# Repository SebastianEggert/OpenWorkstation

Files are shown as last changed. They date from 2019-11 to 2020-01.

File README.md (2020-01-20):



# OpenWorkstation
 An open source and modular workstation concept for life science automation.

 * [Overview](#overview)
 * [OpenWorkstation API](#api)
 * [Development Status](#development_status)
 * [Getting Started](#getting_started)
 * [Contributing](#contributing)

## Overview

We present a general Open Source Hardware concept to develop scientific equipment. The general setup can be customized to fit diverse experimental requirements by adding different numbers and kinds of hardware modules to execute the desired functionality. Within these modules, each hardware module as well as the configuration of the hardware modules can be specifically customized according to the experimental requirements. This ‘drag and drop’ approach enables a high degree of versatility, since the components as well as their configuration can be customized to fit the given requirements.

Specifically, the OpenWorkstation concept provides the following features:

 * Simple and fast development of customized hardware modules
 * Modularity to combine different open source projects
 * Available API to operate modules
 * Hardware and software files are freely accessible

 <p align="center">
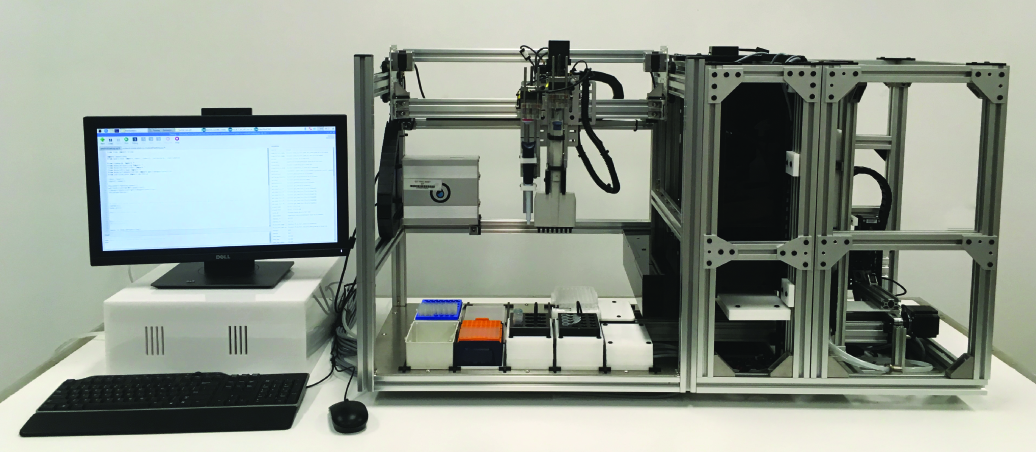
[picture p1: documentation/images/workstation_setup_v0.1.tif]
 </p>

## OpenWorkstation API

Building upon the [Opentrons API](https://github.com/Opentrons/opentrons), the OpenWorkstation API is a simple Python framework designed to allow the operation of hardware modules.

If you are familiar with python and comfortable running ``pip``, you can install OpenWorkstation API by running:

```
pip install openworkstation
```

## Development status

The OpenWorkstation project is an open source project. The concept was developed in the labs of the [ARC Industrial Transformation Training Centre in Additive Biomanufacturing](http://additivebiomanufacturing.org) to simplify the design and development of automated solutions. The OpenWorkstation project remains under active development and new software as well as hardware features continue to be integrated.

Please do no hesitate to [get in touch](mailto:s.eggert@qut.edu.au) to provide feedback and discuss potential applications.

## Getting started

The documentation is divided into the following sections:

 * [Concept](documentation/concept.md) for general information
 * [Pre-requisites and installation](documentation/installation.md) describes what you will need to install the OpenWorkstation API
 * [Programming](documentation/programming.md) provides detailed instructions on writing scripts to operate the modules
 * [Developed module files](hardware/README.md) are available for the present workstation
 * [CAD part library](hardware/README.md) is provided to accelerate the development process for new module
 * [Development plan](documentation/dev_plan.md) outlines future work packages

## Contributing

We are looking for contributors!

[Get in touch](mailto:s.eggert@qut.edu.au)

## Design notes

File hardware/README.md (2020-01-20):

## Hardware

The hardware section is divided into CAD files (SolidWorks) used to build the presented workstation (incl modules) and a parts library to accelerate the development process for new modules in the future.

All hardware files are available for the presented workstation:

 * [Assembled workstation](workstation)
 * [Pipetting module](modulePipetting)  
 * [Crosslinker module](moduleCrosslinker)
 * [Storage module](moduleStorage)
 * [Transport module](moduleTransport)
 * [Base frame](base-frame)

The following libraries are available to support users during the development of new module:

 * [Aluminium profiles](aluminium-profiles)
 * [Module frames](moduleFrame)
 * [OpenBuilds parts](OpenBuilds)

OpenBuilds provides additional support via their [SolidWorks part library](https://openbuilds.com/projectresources/solidworks-2014-parts-library.160/) and the uploaded models on [GrabCAD](https://grabcad.com/openbuilds-1/models).

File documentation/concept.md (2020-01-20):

## Concept

Inspired by industrial assembly lines, we aimed for an approach to engineer a workstation where samples are being transported through customizable and reconfigurable modules. To do so, we developed (i) a modular concept, (ii) customizable hardware modules, and (iii) fully accessible application programming interface (API).

We describe a setup with a modular architecture, wherein we use one module respectively to implement a set of diverse functional elements. The base setup of the assembly line-inspired concept accommodates a pipetting and a transport module as essential elements. A transport module is required to move samples through the modules and, thereby, connects the implemented hardware modules with each other. A pipetting module is installed for essential pipetting operations which are required for almost every in vitro study. This general set up can then be customized to suit diverse experimental requirements by adding different numbers and kinds of hardware modules executing the desired functionality. Within these modules, each hardware module as well as the configuration of the hardware modules can be individually customized according to the experimental requirements. This ‘drag and drop’ approach enables a high degree of versatility, since the components as well as their configuration can be customized to fit the given requirements, including the option to remove components from the platform non-destructively without interfering with the functional operation of the other modules.

<p align="center">
</p>

## General module description

#### Computational module
A computer is utilized to operate the workstation by providing an interface and sending the experimental protocol to the implemented control boards which forward commands to the functional parts of the hardware modules. A Python API has been developed to write protocol scripts to operate the entire workstation, and, thereby, all hardware modules in a synchronized mode. Python has been selected as the main programming language, since it is open source and a high-level and general-purpose dynamic language that focuses on code readability. Some of Python’s main advantages are (i) the extensive support libraries; (ii) the numerous third-party modules via the Python Package Index (PyPI) to enable interactions with other languages and platforms; (iii) the open source character and the community-driven development to facilitate collaborations and ease of use; and (iv) the increased productivity to build scalable multi-protocol network applications.

#### Control board module
A control board translates the received protocol script into a language to operate the functional components of the hardware modules. We selected the smoothieboard (The Smoothie Project, http://smoothieware.org) as the control board module due to the range of available sizes (e.g. from 3x to 5x axis control), the numerous capabilities (e.g. up to 5x axis control with 1/32 microstepping, 6x end stops, up to 3x MOSFETs with 12.5A max, and 3x MOSFETs with 3A max, ethernet and USB connections), the 32-bit microcontroller, the available documentation, and the overall quality to price ratio. The Smoothie Project is an open source project supported by the community to design open source hardware controllers with open source firmware (https://github.com/Smoothieware). The following motion control boards can be recommended as alternatives, but have not been tested and might require additional software engineering for successful implementation: Duet3D , Panucatt Azteeg X5 GT , TinyG CNC Controller Board .

#### Hardware modules
The customized hardware modules operate a set of specific functions required to execute the experiment. The combination of functional components into one hardware module introduces an efficient and agile approach, since a single module can be easily modified without interfering with other modules. To do so, functional components are integrated into an aluminium frame to enable easy module handling and provide a robust solution for moving parts. Moreover, the various connection modes of the aluminium profiles (e.g. t-slots, nuts, threated holes, corner brackets, etc.) enable fast and inexpensive design iterations. Pre-configured aluminium frames as well as assembled mechanical parts (e.g. linear stages) are available for developers as ready-to-use assemblies to support and accelerate the design and development process. Under section 2.4, we demonstrate the feasibility for customized hardware module development and, subsequently, successful adoption of this concept for laboratory automation in the context of a case study.

#### Monitoring modules
As monitoring capability, we understand the measurement of process variables either continuously and/or repeatedly during the course of the experiment. In general, monitoring modules may include camera-based systems or various sensor types (e.g. temperature, pH, oxygen, lactate, etc.) to record the variables and document the changes over time. Implemented functions can also be used in the sense of an in-process control unit to automatically adjust operational variables via advanced process algorithms. Such in-process control units ensure consistent product quality or reach defined product output specifications.

<p align="center">
</p>

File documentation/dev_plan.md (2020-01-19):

## Development Plan

The development plan will provide an overview of current work and future projects.

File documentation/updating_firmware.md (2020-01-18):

# Updating Firmware of Motorcontroller

The project is using smoothieboards to execute implemented functions. The configuration of the connected peripherals (e.g. stepper motor) is stored on the smoothieboard's SD card and has to be updated initially. When parts with a different specification (e.g. step size of a stepper motor) are used, the configuration files have to be modified to accommodate the physical changes. A list of most configuration options is provided by the Smoothie Project (http://smoothieware.org/configuration-options).

The configuration for the developed modules with the implemented parts can be found in the design files section.

Building upon the Opentrons open source products (https://opentrons.com), this project is using Opentrons' firmware for the smoothieboard.

### Download Files

[Download the zipped files from here](https://github.com/opentrons/smoothie-config/archive/1.2.0.zip) and unpack them.

### Update config file
Open `config` file, update specifications for your developed module, such as step size for stepper motor), and save file.

### Update files on the smoothieboard's SD card

Open the SD card of your smoothieboard and copy the `FIRMWARE.CUR` (downloaded from Github) and `config` (updated in the previous step) files onto the SD card.

### Restart

Insert the SD card into the smoothieboard and restart the smoothieboard by connecting the USB or power supply. The board will read the `firmware.bin` file, then save it as `FIRMWARE.CUR`. Functionalities are executed based on the updated `config` file.

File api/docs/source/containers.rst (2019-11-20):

.. _containers:

######################
Containers
######################

We spend a fair amount of time organizing and counting wells when writing Python protocols. This section describes the different ways we can access wells and groups of wells.

************************************

******************
Labware Library
******************

The opentrons API comes with many common labware containers built in. These containers can be loaded into you Python protocol using the ``containers.load()`` method, and the specific name of the labware you need.

`Check out this webpage`__ to see a visualization of all the API's current built-in containers.

__ https://andysigler.github.io/ot-api-containerviz/

Below are a list of some of the most commonly used containers in the API, as well as images for how they look.

If you are interested in using your own container that is not included in the API, please take a look at how to create custom containers using ``containers.create()``, or contact opentrons Support.

.. note::

    All names are case-sensitive, copying and pasting from this list into the protocol editor will ensure no errors are made.

**********************

Point
=====

Use ``point`` when there is only one position per container, such as the trash or a scale. 

.. code-block:: python

    container.load('point', slot)

You can access the point position as ``container.wells('A1')`` or ``container.wells(0)``.

**********************

Tipracks
==========

tiprack-10ul
-------------

Tip rack for a 10 uL pipette (single or 8-channel)

.. code-block:: python

    container.load('tiprack-10ul', slot)

**Accessing Tips:** *single channel* ``['A1']-['H12']``, *8-channel* ``['A1']-['A12']``

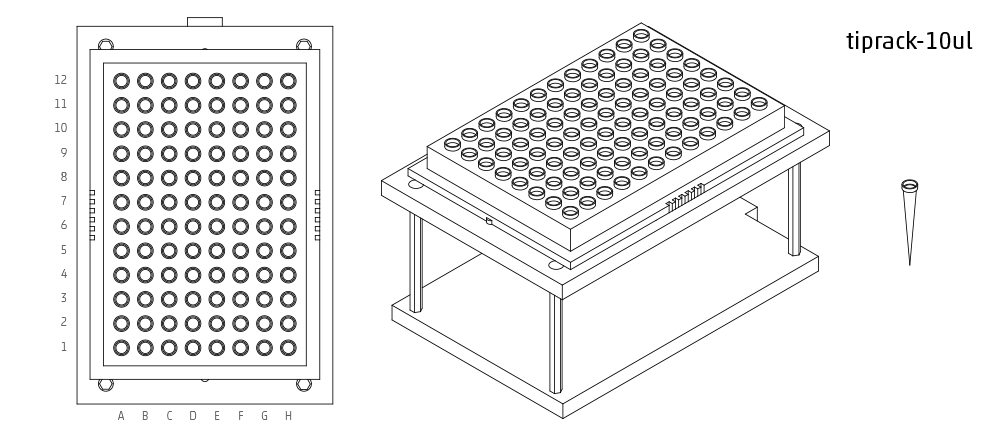
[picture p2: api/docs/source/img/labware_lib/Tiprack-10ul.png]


tiprack-10ul-H
--------------

Tip rack for a single channel 10 uL pipette when the pipette is in the center position.  Set initial position to H1, and the pipette will use all the tips on the right hand side (E-H, 1-12)

.. code-block:: python

    container.load('tiprack-10ul-H', slot)

**Accessing Tips:** *single channel* ``['E-H, 1-12']``

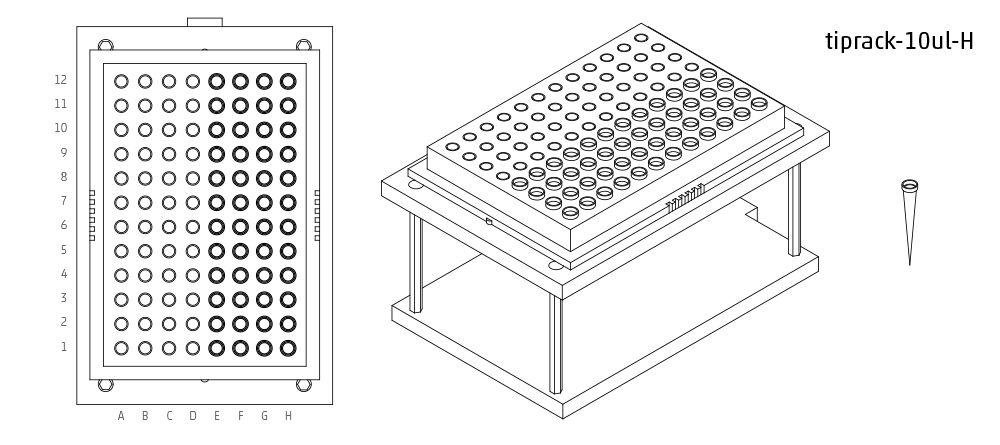
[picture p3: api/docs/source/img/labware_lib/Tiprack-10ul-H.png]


tiprack-200ul
-------------

Tip rack for a 200 or 300 uL pipette (single or 8-channel)

.. code-block:: python

    container.load('tiprack-200ul', slot)

**Accessing Tips:** *single channel* ``['A1']-['H12']``, *8-channel* ``['A1']-['A12']``

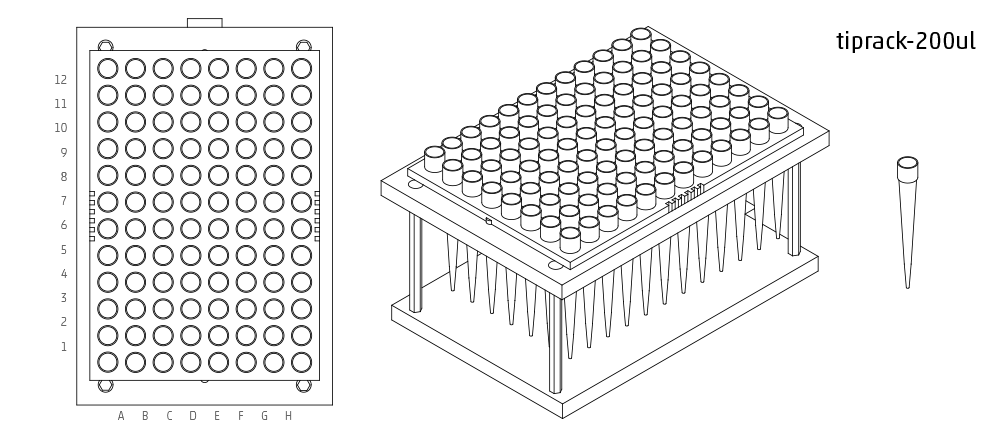
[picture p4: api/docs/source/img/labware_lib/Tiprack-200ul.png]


tiprack-1000ul
--------------

Tip rack for a 1000 uL pipette (single or 8-channel)

.. code-block:: python

    container.load('tiprack-1000ul', slot)

**Accessing Tips:** *single channel* ``['A1']-['H12']``, *8-channel* ``['A1']-['A12']``

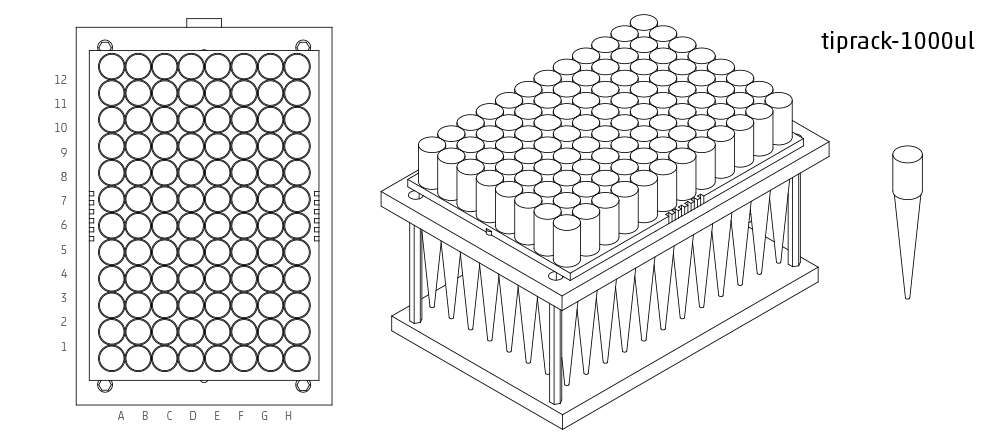
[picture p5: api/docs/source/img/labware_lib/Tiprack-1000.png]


tiprack-1000ul-chem
-------------------

Tip rack for 1000ul chem (10x10)

.. code-block:: python

    container.load('tiprack-1000ul-chem', slot)

**Accessing Tips:** *single channel* ``[0]-[99]``

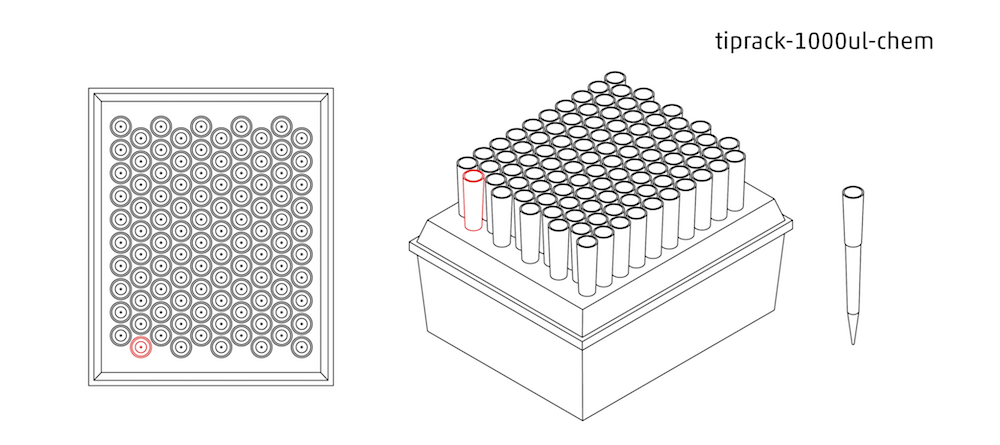
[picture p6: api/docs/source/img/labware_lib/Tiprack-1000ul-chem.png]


**********************

Troughs
========

trough-12row
-------------

12 row reservoir

.. code-block:: python

    container.load('trough-12row', slot)

**Accessing Rows:** *single channel* ``['A1']-['A12']``, *8-channel* ``['A1']-['A12']``

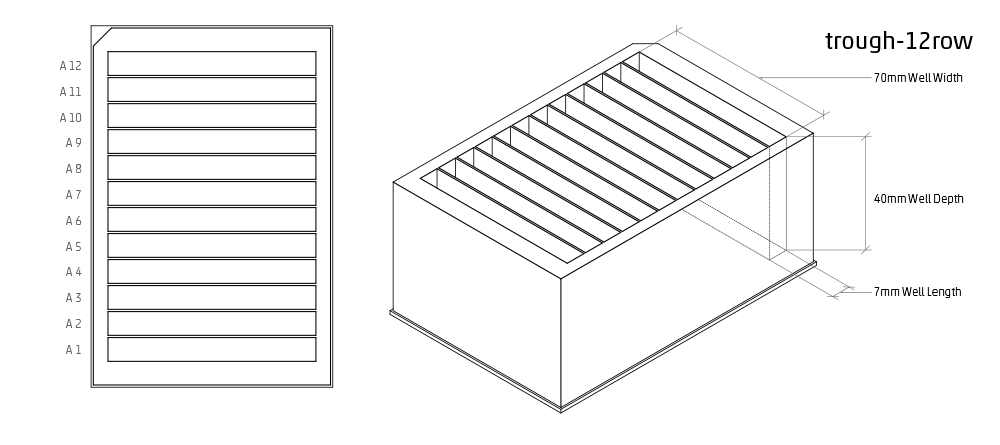
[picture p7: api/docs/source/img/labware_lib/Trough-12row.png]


**********************

Tube Racks
==========

tube-rack-.75ml
-------------

4x6 rack that holds .75 mL microcentrifuge tubes
(A1, A1-D6)

.. code-block:: python

    container.load('tube-rack-.75ml', slot)

**Accessing Tubes:** *single channel* ``['A1']-['D6']``

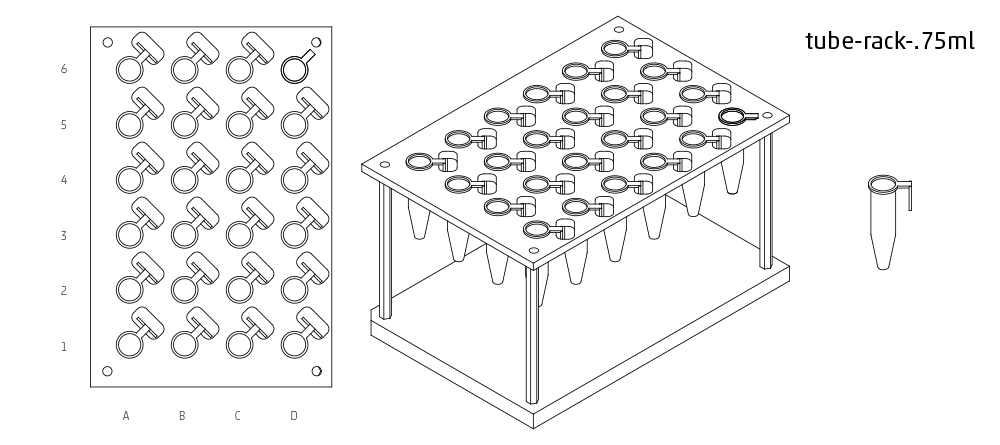
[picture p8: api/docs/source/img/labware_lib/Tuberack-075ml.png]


tube-rack-2ml
-------------

4x6 rack that holds 1.5 mL microcentrifuge tubes and 2 mL microcentrifuge tubes

.. code-block:: python

    container.load('tube-rack-2ml', slot)

**Accessing Tubes:** *single channel* ``['A1']-['D6']``

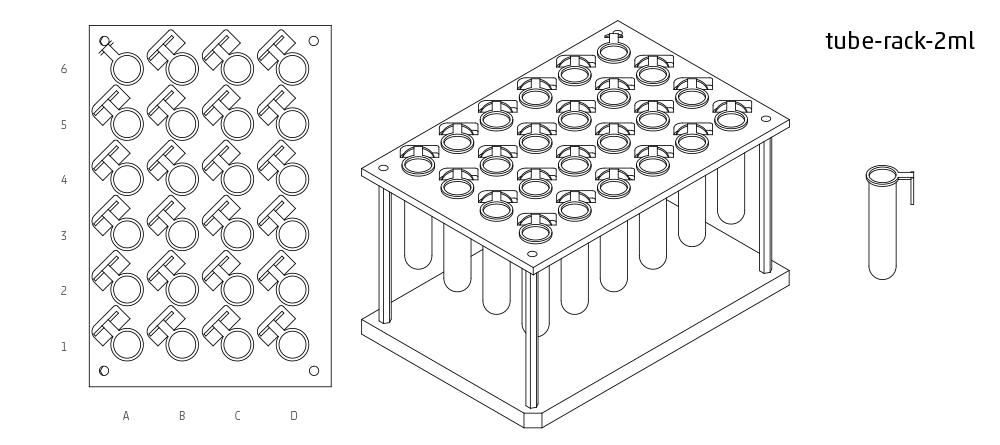
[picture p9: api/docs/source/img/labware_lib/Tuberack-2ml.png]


tube-rack-15_50ml
------------------

rack that holds 6 15 mL tubes and 4 50 mL tubes

.. code-block:: python

    container.load('tube-rack-15_50ml', slot)

**Accessing Tubes:** *single channel* ``['A1']-['A3'], ['B1']-['B3'], ['C1']-['C2'], ['D1']-['D2']``

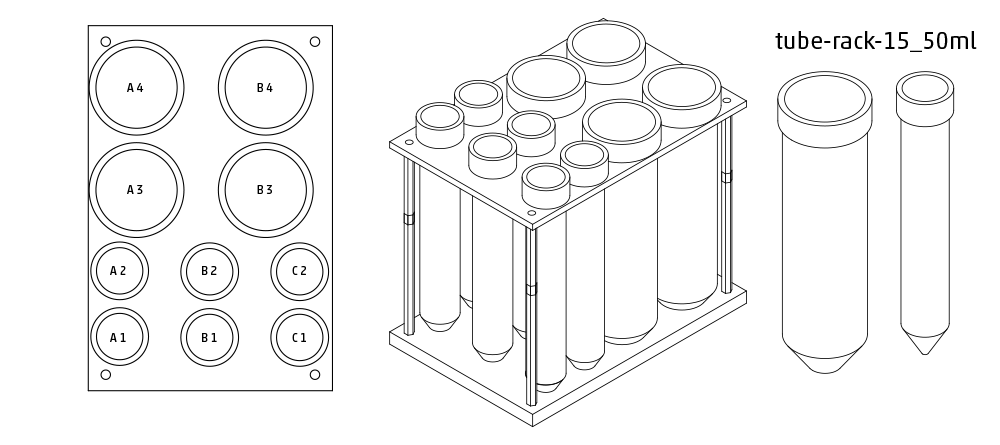
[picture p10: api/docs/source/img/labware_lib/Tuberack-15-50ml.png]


Plates
=======

96-deep-well
-------------

See dimensions in diagram below.

.. code-block:: python

    container.load('96-deep-well', slot)

**Accessing Wells:** *single channel* ``['A1']-['H12']``, *8-channel* ``['A1']-['A12']``

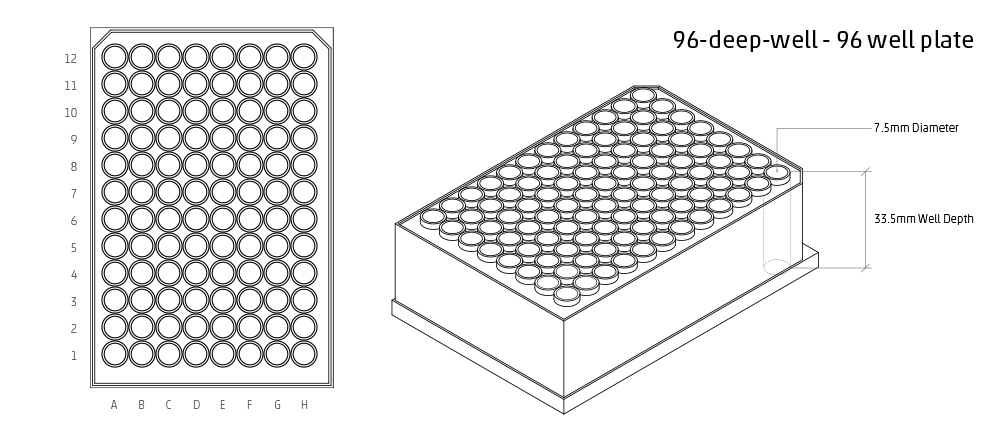
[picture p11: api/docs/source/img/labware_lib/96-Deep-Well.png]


96-PCR-tall
-------------

See dimensions in diagram below.

.. code-block:: python

    container.load('96-PCR-tall', slot)

**Accessing Wells:** *single channel* ``['A1']-['H12']``, *8-channel* ``['A1']-['A12']``

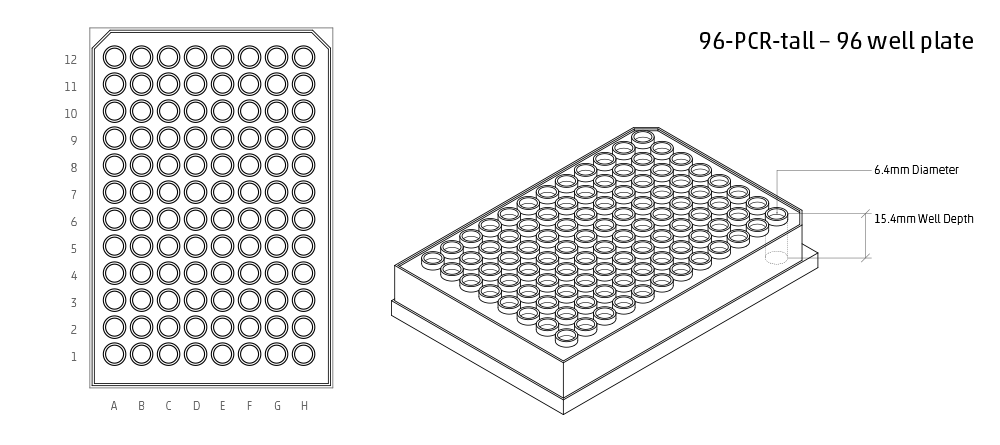
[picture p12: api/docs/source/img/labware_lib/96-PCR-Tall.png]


96-PCR-flat
-------------

See dimensions in diagram below.

.. code-block:: python

    container.load('96-PCR-flat', slot)

**Accessing Wells:** *single channel* ``['A1']-['H12']``, *8-channel* ``['A1']-['A12']``

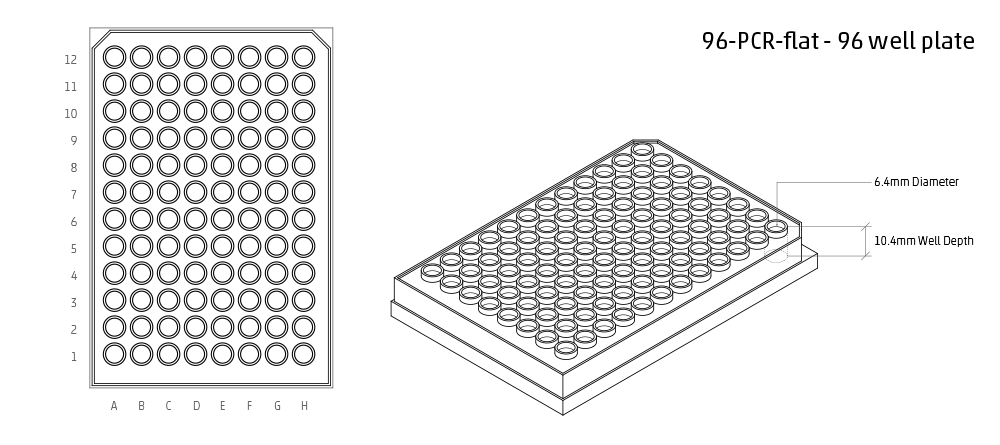
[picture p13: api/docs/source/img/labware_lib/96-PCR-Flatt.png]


PCR-strip-tall
----------------

See dimensions in diagram below.

.. code-block:: python

    container.load('PCR-strip-tall', slot)

**Accessing Wells:** *single channel* ``['A1']-['A8']``, *8-channel* ``['A1']``

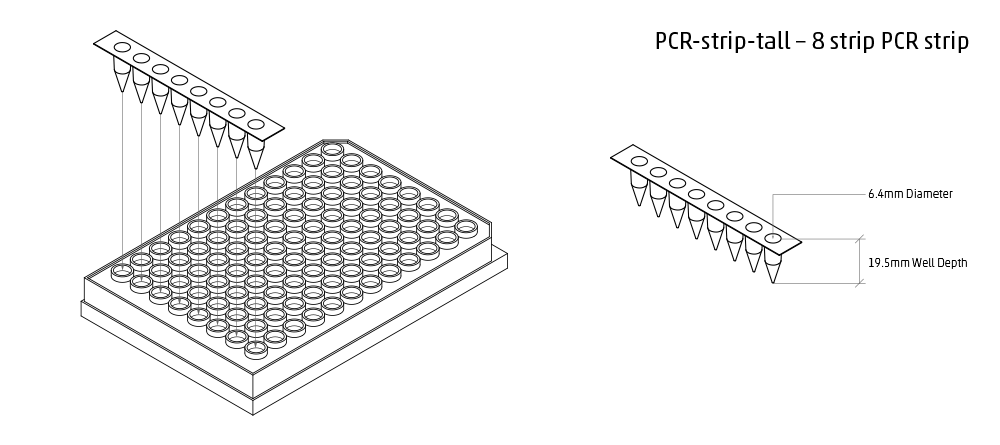
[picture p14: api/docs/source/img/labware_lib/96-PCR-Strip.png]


384-plate
----------

See dimensions in diagram below.

.. code-block:: python

    container.load('384-plate', slot)

**Accessing Wells:** *single channel* ``['A1']-['P24']``, *multi-channel* ``['A1']-['A24]``

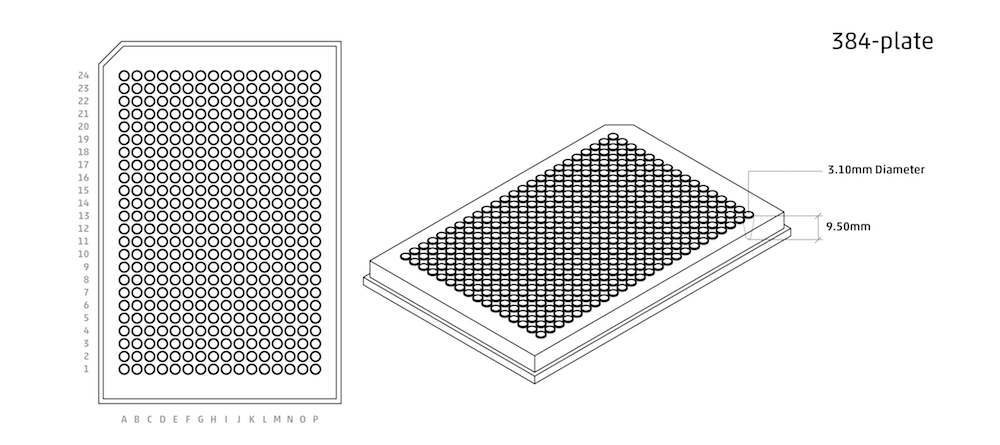
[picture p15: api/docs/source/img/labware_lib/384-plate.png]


**********************

.. testsetup:: containers

    from opentrons import containers, robot
    robot.reset()

**************
Containers
**************

The containers module allows you to load common labware into your protocol. `Go here`__ to see a visualization of all built-in containers.

__ https://andysigler.github.io/ot-api-containerviz/

.. testcode:: containers

    '''
    Examples in this section require the following
    '''
    from opentrons import containers

List
====

Once the container module is loaded, you can see a list of all containers currently inside the API by calling ``containers.list()``

.. testcode:: containers

    containers.list()

Load
====

Labware is loaded with two arguments: 1) the container type, and 2) the deck slot it will be placed in on the robot.

.. testcode:: containers

    p = containers.load('96-flat', 'B1')

A third optional argument can be used to give a container a unique name.

.. testcode:: containers

    p = containers.load('96-flat', 'B1', 'any-name-you-want')

Unique names are useful in a few scenarios. First, they allow the container to have independant calibration data from other containers in the same slot. In the example above, the container named 'any-name-you-want' will assume different calibration data from the unnamed plate, even though they are the same type and in the same slot.

.. note::

    Calibration data refers to the saved positions for each container on deck, and is a part of the `opentrons App calibration procedure`__.

__ https://opentrons.com/getting-started/calibrate-deck

Names can also be used to place multiple containers in the same slot all at once. For example, the flasks below are all placed in slot D1. So in order for the opentrons API to tell them apart, we have given them each a unique name.

.. testcode:: containers

    fa = containers.load('T25-flask', 'D1', 'flask_a')
    fb = containers.load('T25-flask', 'D1', 'flask_b')
    fc = containers.load('T25-flask', 'D1', 'flask_c')

Create
======

In addition to the default containers that come with the opentrons API, you can create your own custom containers.

Through the API's call containers.create(), you can create simple grid containers, which consist of circular wells arranged in columns and rows.

.. testcode:: containers

    containers.create(
        '3x6_plate',                    # name of you container
        grid=(3, 6),                    # specify amount of (columns, rows)
        spacing=(12, 12),               # distances (mm) between each (column, row)
        diameter=5,                     # diameter (mm) of each well on the plate
        depth=10)                       # depth (mm) of each well on the plate

When you create your custom container, then it will be saved for later use under the name you've given it. This means you can use containers.load() to use the custom container you've created in this and any future protocol.

.. testcode:: containers

    custom_plate = containers.load('3x6_plate', 'D1')

    for well in custom_plate.wells():
        print(well)

will print out...

.. testoutput:: containers
    :options: -ELLIPSIS, +NORMALIZE_WHITESPACE

    <Well A1>
    <Well B1>
    <Well C1>
    <Well A2>
    <Well B2>
    <Well C2>
    <Well A3>
    <Well B3>
    <Well C3>
    <Well A4>
    <Well B4>
    <Well C4>
    <Well A5>
    <Well B5>
    <Well C5>
    <Well A6>
    <Well B6>
    <Well C6>

.. testsetup:: pipettes

    from opentrons import instruments, robot
    robot.reset()

**********************

.. testsetup:: individualwells

    from opentrons import containers, robot

    robot.reset()
    plate = containers.load('96-flat', 'A1')

******************
Accessing Wells
******************

**********************

Individual Wells
================

When writing a protocol using the API, you will be spending most of your time selecting which wells to transfer liquids to and from.

The OT-One deck and containers are all set up with the same coordinate system - numbered rows and lettered columns.

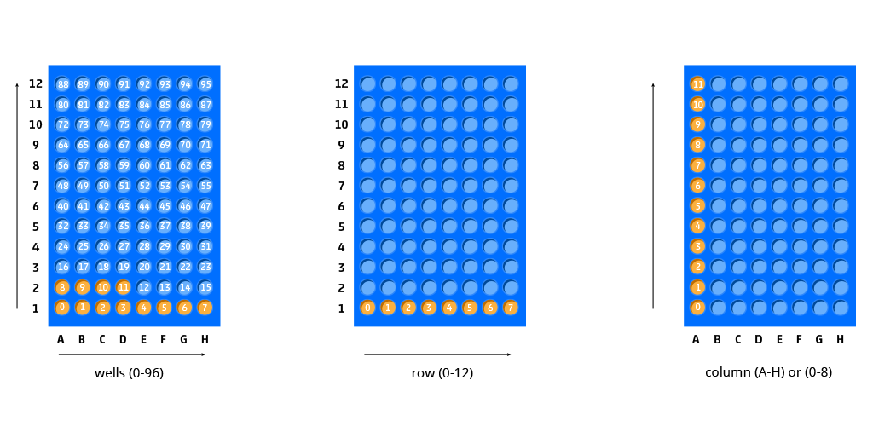
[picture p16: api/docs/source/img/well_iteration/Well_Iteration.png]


.. testcode:: individualwells
    
    '''
    Examples in this section expect the following
    '''
    from opentrons import containers

    plate = containers.load('96-flat', 'A1')

Wells by Name
-------------

Once a container is loaded into your protocol, you can easily access the many wells within it using ``wells()`` method. ``wells()`` takes the name of the well as an argument, and will return the well at that location.

.. testcode:: individualwells

    plate.wells('A1')
    plate.wells('H12')

Wells by Index
--------------

Wells can be referenced by their "string" name, as demonstrated above. However, they can also be referenced with zero-indexing, with the first well in a container being at position 0.

.. testcode:: individualwells

    plate.wells(0)   # well A1
    plate.wells(95)  # well H12
    plate.wells(-1)  # well H12 (Python let's you do this)

Columns and Rows
----------------

A container's wells are organized within a series of columns and rows, which are also labelled on standard labware. In the API, columns are given letter names (``'A'`` through ``'H'`` for example) and go left to right, while rows are given numbered names (``'1'`` through ``'8'`` for example) and go from front to back.
You can access a specific row or column by using the ``rows()`` and ``cols()`` methods on a container. These will return all wells within that row or column.

.. testcode:: individualwells

    column = plate.cols('A')
    row = plate.rows('1')

    print('Column "A" has', len(column), 'wells')
    print('Row "1" has', len(row), 'wells')

will print out...

.. testoutput:: individualwells
    :options: -ELLIPSIS, +NORMALIZE_WHITESPACE

    Column "A" has 12 wells
    Row "1" has 8 wells

The ``rows()`` or ``cols()`` methods can be used in combination with the ``wells()`` method to access wells within that row or column. In the example below, both lines refer to well ``'A1'``.

.. testcode:: individualwells

    plate.cols('A').wells('1')
    plate.rows('1').wells('A')

**********************

.. testsetup:: multiwells

    from opentrons import containers, robot

    robot.reset()
    plate = containers.load('96-flat', 'A1')

Multiple Wells
==============

If we had to reference each well one at a time, our protocols could get very very long.

When describing a liquid transfer, we can point to groups of wells for the liquid's source and/or destination. Or, we can get a group of wells that we want to loop through.

.. testcode:: multiwells
    
    '''
    Examples in this section expect the following
    '''
    from opentrons import containers

    plate = containers.load('96-flat', 'B1')

Wells
-----

The ``wells()`` method can return a single well, or it can return a list of wells when multiple arguments are passed.

Here is an example or accessing a list of wells, each specified by name:

.. testcode:: multiwells

    w = plate.wells('A1', 'B2', 'C3', 'H12')

    print(w)

will print out...

.. testoutput:: multiwells
    :options: -ELLIPSIS, +NORMALIZE_WHITESPACE

    <WellSeries: <Well A1><Well B2><Well C3><Well H12>>

Multiple wells can be treated just like a normal Python list, and can be iterated through:

.. testcode:: multiwells

    for w in plate.wells('A1', 'B2', 'C3', 'H12'):
        print(w)

will print out...

.. testoutput:: multiwells
    :options: -ELLIPSIS, +NORMALIZE_WHITESPACE

    <Well A1>
    <Well B2>
    <Well C3>
    <Well H12>

Wells To
--------

Instead of having to list the name of every well, we can also create a range of wells with a start and end point. The first argument is the starting well, and the ``to=`` argument is the last well.

.. testcode:: multiwells
    
    for w in plate.wells('A1', to='H1'):
        print(w)

will print out...

.. testoutput:: multiwells
    :options: -ELLIPSIS, +NORMALIZE_WHITESPACE

    <Well A1>
    <Well B1>
    <Well C1>
    <Well D1>
    <Well E1>
    <Well F1>
    <Well G1>
    <Well H1>

Not only can we get every well between the start and end positions, but we can also set the ``step=`` size. The example below will access every 2nd well between ``'A1'`` and ``'H'``:

.. testcode:: multiwells
    
    for w in plate.wells('A1', to='H1', step=2):
        print(w)

will print out...

.. testoutput:: multiwells
    :options: -ELLIPSIS, +NORMALIZE_WHITESPACE

    <Well A1>
    <Well C1>
    <Well E1>
    <Well G1>

These lists of wells can also move in the reverse direction along your container. For example, setting the ``to=`` argument to a well that comes before the starting position is allowed:

.. testcode:: multiwells
    
    for w in plate.wells('H1', to='A1', step=2):
        print(w)

will print out...

.. testoutput:: multiwells
    :options: -ELLIPSIS, +NORMALIZE_WHITESPACE

    <Well H1>
    <Well F1>
    <Well D1>
    <Well B1>

Wells Length
------------

Another way you can create a list of wells is by specifying the length= of the well list you need, in addition to the starting point. The example below will return eight wells, starting at well ``'A1'``:

.. testcode:: multiwells
    
    for w in plate.wells('A1', length=8):
        print(w)

will print out...

.. testoutput:: multiwells
    :options: -ELLIPSIS, +NORMALIZE_WHITESPACE

    <Well A1>
    <Well B1>
    <Well C1>
    <Well D1>
    <Well E1>
    <Well F1>
    <Well G1>
    <Well H1>

And just like before, we can also set the ``step=`` argument. Except this time the example will be accessing every 3rd well, until a total of eight wells have been found:

.. testcode:: multiwells
    
    for w in plate.wells('A1', length=8, step=3):
        print(w)

will print out...

.. testoutput:: multiwells
    :options: -ELLIPSIS, +NORMALIZE_WHITESPACE

    <Well A1>
    <Well D1>
    <Well G1>
    <Well B2>
    <Well E2>
    <Well H2>
    <Well C3>
    <Well F3>

You can set the step= value to a negative number to move in the reverse direction along the container:

.. testcode:: multiwells
    
    for w in plate.wells('H11', length=8, step=-1):
        print(w)

will print out...

.. testoutput:: multiwells
    :options: -ELLIPSIS, +NORMALIZE_WHITESPACE

    <Well H11>
    <Well G11>
    <Well F11>
    <Well E11>
    <Well D11>
    <Well C11>
    <Well B11>
    <Well A11>

Columns and Rows
----------------

Columns and Rows
The same arguments described above can be used with ``rows()`` and ``cols()`` to create lists of rows or columns.

Here is an example of iterating through rows:

.. testcode:: multiwells

    for r in plate.rows('2', length=3, step=-2):
        print(r)

will print out...

.. testoutput:: multiwells
    :options: -ELLIPSIS, +NORMALIZE_WHITESPACE

    <WellSeries: <Well A2><Well B2><Well C2><Well D2><Well E2><Well F2><Well G2><Well H2>>
    <WellSeries: <Well A12><Well B12><Well C12><Well D12><Well E12><Well F12><Well G12><Well H12>>
    <WellSeries: <Well A10><Well B10><Well C10><Well D10><Well E10><Well F10><Well G10><Well H10>>

And here is an example of iterating through columns:

.. testcode:: multiwells

    for c in plate.cols('B', to='F', step=2):
        print(c)

will print out...

.. testoutput:: multiwells
    :options: -ELLIPSIS, +NORMALIZE_WHITESPACE

    <WellSeries: <Well B1><Well B2><Well B3><Well B4><Well B5><Well B6><Well B7><Well B8><Well B9><Well B10><Well B11><Well B12>>
    <WellSeries: <Well D1><Well D2><Well D3><Well D4><Well D5><Well D6><Well D7><Well D8><Well D9><Well D10><Well D11><Well D12>>
    <WellSeries: <Well F1><Well F2><Well F3><Well F4><Well F5><Well F6><Well F7><Well F8><Well F9><Well F10><Well F11><Well F12>>

Slices
------

Containers can also be treating similarly to Python lists, and can therefore handle slices.

.. testcode:: multiwells

    for w in plate[0:8:2]:
        print(w)

will print out...

.. testoutput:: multiwells
    :options: -ELLIPSIS, +NORMALIZE_WHITESPACE

    <Well A1>
    <Well C1>
    <Well E1>
    <Well G1>

The API's containers are also prepared to take string values for the slice's ``start`` and ``stop`` positions.

.. testcode:: multiwells

    for w in plate['A1':'A2':2]:
        print(w)

will print out...

.. testoutput:: multiwells
    :options: -ELLIPSIS, +NORMALIZE_WHITESPACE

    <Well A1>
    <Well C1>
    <Well E1>
    <Well G1>

.. testcode:: multiwells

    for w in plate.cols['B']['1'::2]:
        print(w)

will print out...

.. testoutput:: multiwells
    :options: -ELLIPSIS, +NORMALIZE_WHITESPACE

    <Well B1>
    <Well B3>
    <Well B5>
    <Well B7>
    <Well B9>
    <Well B11>

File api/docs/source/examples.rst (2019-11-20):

.. _examples:

########
Examples
########

.. testsetup:: examples

  from opentrons import robot, containers, instruments

  plate = containers.load('96-flat', 'B1')
  trough = containers.load('trough-12row', 'C1')

  tiprack_1 = containers.load('tiprack-200ul', 'A1')
  tiprack_2 = containers.load('tiprack-200ul', 'A2')
      
  p200 = instruments.Pipette(
      axis="b",
      max_volume=200,
      tip_racks=[tiprack_2]) 

All examples on this page assume the following containers and pipette:

.. testcode:: examples

  from opentrons import robot, containers, instruments

  plate = containers.load('96-flat', 'B1')
  trough = containers.load('trough-12row', 'C1')

  tiprack_1 = containers.load('tiprack-200ul', 'A1')
  tiprack_2 = containers.load('tiprack-200ul', 'A2') 
      
  p200 = instruments.Pipette(
      axis="b",
      max_volume=200,
      tip_racks=[tiprack_2])

******************************

***************
Basic Transfer
***************

Moving 100uL from one well to another:

.. testcode:: examples
  
  p200.transfer(100, plate.wells('A1'), plate.wells('B1'))

If you prefer to not use the ``.transfer()`` command, the following pipette commands will create the some results:

.. testcode:: examples

  p200.pick_up_tip()
  p200.aspirate(100, plate.wells('A1'))
  p200.dispense(100, plate.wells('A1'))
  p200.return_tip()

******************************

*****
Loops
*****

Loops in Python allows your protocol to perform many actions, or act upon many wells, all within just a few lines. The below example loops through the numbers ``0`` to ``11``, and uses that loop's current value to transfer from all wells in a trough to each row of a plate:

.. testcode:: examples

  # distribute 20uL from trough:A1 -> plate:row:1
  # distribute 20uL from trough:A2 -> plate:row:2
  # etc...

  # ranges() starts at 0 and stops at 12, creating a range of 0-11
  for i in range(12):
    p200.distribute(20, trough.wells(i), plate.rows(i))

******************************

*******************
Multiple Air Gaps
*******************

The opentrons liquid handler can do some things that a human cannot do with a pipette, like accurately alternate between aspirating and creating air gaps within the same tip. The below example will aspirate from five wells in the trough, while creating a air gap between each sample.

.. testcode:: examples
  
  p200.pick_up_tip()

  for well in trough.wells():
    p200.aspirate(5, well).air_gap(10)

  p200.dispense(plate.wells('A1'))

  p200.return_tip()

******************************

***************
Dilution
***************

This example first spreads a dilutent to all wells of a plate. It then dilutes 8 samples from the trough across the 8 columns of the plate.

.. testcode:: examples

  p200.distribute(50, trough.wells('A12'), plate.wells())  # dilutent

  # loop through each column
  for i in range(8):

    # save the source well and destination column to variables
    source = trough.wells(i)
    column = plate.cols(i)

    # transfer 10uL of source to first well in column
    p200.transfer(10, source, column.wells('1'))

    # dilute the sample down the column
    p200.transfer(
      10, column.wells('1', to='11'), column.wells('2', to='12'),
      mix_after=(3, 25))

******************************

***************
Plate Mapping
***************

Deposit various volumes of liquids into the same plate of wells, and automatically refill the tip volume when it runs out.

.. testcode:: examples

  # these uL values were created randomly for this example
  water_volumes = [
    1,  2,  3,  4,  5,  6,  7,  8,
    9,  10, 11, 12, 13, 14, 15, 16,
    17, 18, 19, 20, 21, 22, 23, 24,
    25, 26, 27, 28, 29, 30, 31, 32,
    33, 34, 35, 36, 37, 38, 39, 40,
    41, 42, 43, 44, 45, 46, 47, 48,
    49, 50, 51, 52, 53, 54, 55, 56,
    57, 58, 59, 60, 61, 62, 63, 64,
    65, 66, 67, 68, 69, 70, 71, 72,
    73, 74, 75, 76, 77, 78, 79, 80,
    81, 82, 83, 84, 85, 86, 87, 88,
    89, 90, 91, 92, 93, 94, 95, 96
  ]

  p200.distribute(water_volumes, trough.wells('A12'), plate)

The final volumes can also be read from a CSV, and opened by your protocol.

.. code-block:: python

  '''
    This example uses a CSV file saved on the same computer, formatted as follows,
    where the columns in the file represent the 8 columns of the plate,
    and the rows in the file represent the 12 rows of the plate,
    and the values represent the uL that must end up at that location

    1,  2,  3,  4,  5,  6,  7,  8,
    9,  10, 11, 12, 13, 14, 15, 16,
    17, 18, 19, 20, 21, 22, 23, 24,
    25, 26, 27, 28, 29, 30, 31, 32,
    33, 34, 35, 36, 37, 38, 39, 40,
    41, 42, 43, 44, 45, 46, 47, 48,
    49, 50, 51, 52, 53, 54, 55, 56,
    57, 58, 59, 60, 61, 62, 63, 64,
    65, 66, 67, 68, 69, 70, 71, 72,
    73, 74, 75, 76, 77, 78, 79, 80,
    81, 82, 83, 84, 85, 86, 87, 88,
    89, 90, 91, 92, 93, 94, 95, 96,

  '''

  # open file with absolute path (will be different depending on operating system)
  # file paths on Windows look more like 'C:\\path\\to\\your\\csv_file.csv'
  with open('/path/to/your/csv_file.csv') as my_file:

      # save all volumes from CSV file into a list
      volumes = []

      # loop through each line (the plate's columns)
      for l in my_file.read().splitlines():
          # loop through each comma-separated value (the plate's rows)
          for v in l.split(','):
              volumes.append(float(v))  # save the volume

      # distribute those volumes to the plate
      p200.distribute(volumes, trough.wells('A1'), plate.wells())

******************************

*******************
Precision Pipetting
*******************

This example shows how to deposit liquid around the edge of a well.

.. testcode:: examples

  p200.pick_up_tip()

  # rotate around the edge of the well, dropping 10ul at a time
  theta = 0.0
  while p200.current_volume > 0:
      # we can move around a circle with radius (r) and theta (degrees)
      well_edge = plate.wells('B1').from_center(r=1.0, theta=theta, h=0.9)
      
      # combine a Well with a Vector in a tuple
      destination = (plate.wells('B1'), well_edge)
      p200.move_to(destination, strategy='direct')  # move straight there
      p200.dispense(10)
      
      theta += 0.314

  p200.drop_tip()

******************************

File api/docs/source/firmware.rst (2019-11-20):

.. _firmware:

================
Firmware Updates
================

The motorcontroller inside all opentrons liquid handlers (called Smoothieboard or just Smoothie) will need it's firmware updated if you are planning to use the opentrons API and accompanying 2.0 app. The process is simple, and can be done from your computer in under a minute.

To summarize, there are two files on your Smoothie that must be replaced; ``FIRMWARE.CUR`` and ``config``. 

Download Files
----------------------

Download the zipped files from here:

https://github.com/opentrons/smoothie-config/archive/2.0.0.zip

After downloading, unpack the zip file to view its contents. The latest firmware files are found in folder "v2.0.0".

Open the Smoothie's MicroSD Card
---------------------------------

Power OFF and unplug your opentrons liquid handler's USB cable. Remove the microSD card from Smoothieboard (just above the USB connector on the robot), and connect it to your personal computer or laptop. It will show up as a storage device on your computer.

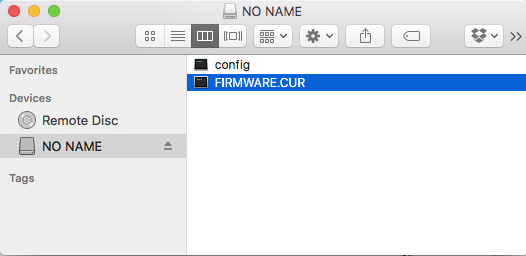
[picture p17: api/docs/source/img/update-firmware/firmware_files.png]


Open the microSD storage device to see it's ``FIRMWARE.CUR`` and ``config`` files. There might be other files there, but the two you need to worry about are ``FIRMWARE.CUR`` and ``config``, because these are what we will be replacing.

Select Your Model's Config
----------------------------------

opentrons `come in three models`__, the Standard, Pro, and Hood. Each model requires a unique ``config`` and ``firmware.bin`` file to go along with it. Find the files that matches your robot (the folders are named after each model).

__ https://opentrons.com/robots

** Note: We have release a "Plus" version of our robots, which have faster motors. If you received a robot after April 2017, and if your robot's Z motor is all black (no silver on the outside) than you have a "Plus" model.

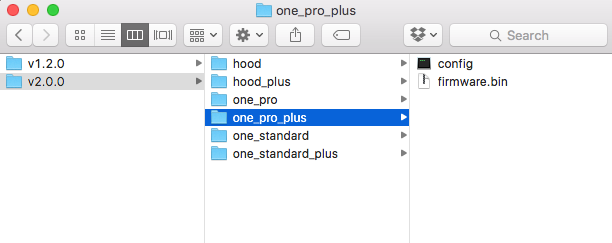
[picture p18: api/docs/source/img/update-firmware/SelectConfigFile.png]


Copy Over Files
---------------------------------

Drag both the ``config`` file and ``firmware.bin`` from the correct folder onto the microSD card. You will be overwriting the old ``config`` file, so your computer may ask if you would like to proceed with replacing it.



The contents of the microSD card should now look like this:

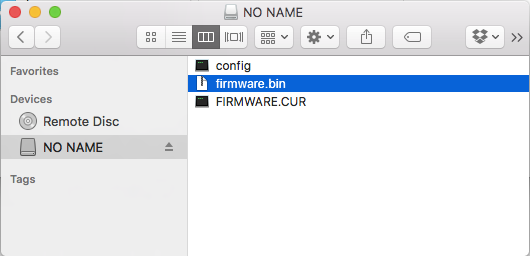
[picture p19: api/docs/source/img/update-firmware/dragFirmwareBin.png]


Restart
---------------

Unmount the Smoothie's microSD card from your computer, and connect it back to your powered OFF robot. When the robot powers on, it will read the ``firmware.bin`` file, then save it as ``FIRMWARE.CUR``. It will then read the new ``config`` file, and your liquid handler now has updated firmware.

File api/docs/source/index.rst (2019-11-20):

.. opentrons API documentation master file, created by
   sphinx-quickstart on Thu Oct 27 12:10:26 2016.
   You can adapt this file completely to your liking, but it should at least
   contain the root `toctree` directive.

===============
opentrons API
===============

The opentrons API is a simple framework designed to make writing automated biology lab protocols easy.

We’ve designed it in a way we hope is accessible to anyone with basic computer and wetlab skills. As a bench scientist, you should be able to code your automated protocols in a way that reads like a lab notebook.

`View source code on GitHub`__

__ https://github.com/opentrons/opentrons-api

**********************

.. testsetup::  helloworld

    from opentrons import containers, instruments, robot

    robot.reset()

    tiprack = containers.load('tiprack-200ul', 'A1')
    plate = containers.load('96-flat', 'B1')

    pipette = instruments.Pipette(axis='b', max_volume=200)

How it Looks
---------------

The design goal of the opentrons API is to make code readable and easy to understand. For example, below is a short set of instruction to transfer from well ``'A1'`` to well ``'B1'`` that even a computer could understand:

.. code-block:: none

    Use the opentrons API's containers and instruments

    Add a 96 well plate, and place it in slot 'B1'
    Add a 200uL tip rack, and place it in slot 'A1'

    Add a 200uL pipette to axis 'b', and tell it to use that tip rack

    Transfer 100uL from the plate's 'A1' well to it's 'A2' well

If we were to rewrite this with the opentrons API, it would look like the following:

.. testcode::  helloworld

    # imports
    from opentrons import containers, instruments

    # containers
    plate = containers.load('96-flat', 'B1')
    tiprack = containers.load('tiprack-200ul', 'A1')

    # pipettes
    pipette = instruments.Pipette(axis='b', max_volume=200, tip_racks=[tiprack])

    # commands
    pipette.transfer(100, plate.wells('A1'), plate.wells('B1'))

**********************

How it's Organized
------------------

When writing protocols using the opentrons API, there are generally three sections:

1) Imports
2) Containers
3) Pipettes
4) Commands

Imports
^^^^^^^

When writing in Python, you must always include the opentrons API within your file. We most commonly use the ``containers`` and ``instruments`` sections of the API.

From the example above, the "imports" section looked like:

.. code-block::  python

    from opentrons import containers, instruments

Containers
^^^^^^^^^^

While the imports section is usually the same across protocols, the containers section is different depending on the tip racks, well plates, troughs, or tubes you're using on the robot.

Each container is given a type (ex: ``'96-flat'``), and the slot on the robot it will be placed (ex: ``'B1'``).

From the example above, the "containers" section looked like:

.. code-block::  python

    plate = containers.load('96-flat', 'B1')
    tiprack = containers.load('tiprack-200ul', 'A1')

Pipettes
^^^^^^^^

Next, pipettes are created and attached to a specific axis on the OT-One (``'a'`` or ``'b'``). Axis ``'a'`` is on the center of the head, while axis ``'b'`` is on the left.

There are other parameters for pipettes, but the most important are the ``max_volume`` to set it's size, and the tip rack(s) it will use during the protocol.

From the example above, the "pipettes" section looked like:

.. code-block::  python

    pipette = instruments.Pipette(axis='b', max_volume=200, tip_racks=[tiprack])

Commands
^^^^^^^^

And finally, the most fun section, the actual protocol commands! The most common commands are ``transfer()``, ``aspirate()``, ``dispense()``, ``pick_up_tip()``, ``drop_tip()``, and much more.

This section can tend to get long, relative to the complexity of your protocol. However, with a better understanding of Python you can learn to compress and simplify even the most complex-seeming protocols.

From the example above, the "commands" section looked like:

.. code-block:: python

    pipette.transfer(100, plate.wells('A1'), plate.wells('B1'))

Table of Contents
-----------------

.. toctree::
  :maxdepth: 3

  writing
  containers
  pipettes
  transfer
  robot
  modules
  examples
  api
  calibration
  firmware

.. |br| raw:: html

   <br />

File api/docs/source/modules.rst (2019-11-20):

.. _modules:

################
Hardware Modules
################

**********************

**********
Heat Deck
**********

The heat deck runs off the opensource platform Arduino, which is how you can control it's temperature. Our heat decks come automatically set to reach a temperature of 55 deg Celsius, but you can edit this value by editing the Arduino file.

Find our Heat Deck source code `on GitHub here`__, and download.

__ https://github.com/opentrons/opentrons-modules

Also download and install the `Arduino IDE`__.

__ https://www.arduino.cc/en/main/software

Open the file, and you will see detailed instruction for how to update the temperature. The overiew is that you simply set the number for what temperature you want, then upload that code to the Heat Deck.

**********************

**********
Magbead
**********

Setting up Hardware
^^^^^^^^^^^^^^^^^^^^^^^^^^^^^

Use your included DIY Mag Bead kit to configure the motor control board (see kit instructions).

Initializing Module in API
============================

Just like a pipette, you need to set up and name your module.

**instruments.Magbead** (*mofset, name*)

	* **mosfet -** integer 0-5 (defaults to 0)
	* **name -** the name you want to call your module

.. testsetup:: main

  from opentrons import instruments
  from opentrons.instruments import Pipette
  p200 = instruments.Pipette(axis="b", max_volume=200)

.. testcode:: main

	mag_deck = instruments.Magbead(name='mag_deck')

Activate and Deactivate Magnets 
================================

To activate the magnets and raise the module's platform, run ``.engage()``:

**module.engage** ()

.. testcode:: main

	mag_deck.engage()

To deactivate the magnets and lower the module's platform, run ``.disengage()``:

**module.disengage** ()

.. testcode:: main

	mag_deck.disengage()

Chain Other Commands
============================

Just like ``aspirate()`` and ``dispense()`` can be chained, you can chain ``engage()`` and ``disengage()``, as well as the ``delay()`` if you don't want to do anything between engaging and disengaging the magnets.

.. testcode:: main

	mag_deck.engage()
	mag_deck.delay(60)
	mag_deck.disengage()

	mag_deck.engage().delay(60).disengage()

You can call ``delay()`` with a ``Pipette`` or a ``Magbead`` module.

.. testcode:: main

	p200.delay(10)
	mag_deck.delay(10)

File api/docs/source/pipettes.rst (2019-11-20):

.. _pipettes:

########################
Liquid Handling
########################

The ``instruments`` module gives your protocol access to the ``Pipette``, which is what you will be primarily using to create protocol commands.

************************

******************
Creating a Pipette
******************

.. testcode:: pipettes

    '''
    Examples in this section require the following
    '''
    from opentrons import instruments

Axis and Max Volume
===================

To create a ``Pipette``, you must give it an axis and a max_volume. The axis can be either ``'a'`` or ``'b'``, and the volume is whatever your hand pipette is calibrated for. In this example, we are using a 200uL pipette.

.. testcode:: pipettes

    pipette = instruments.Pipette(
        axis='b',
        name='my-p200',
        max_volume=200)

Minimum Volume
==============

The minimum allowed volume can be set for each pipette. If your protocol attempts to aspirate or dispense a volume below this volume, the API will give you a warning.

.. testcode:: pipettes

    pipette = instruments.Pipette(
        axis='b',
        name='my-p200',
        max_volume=200,
        min_volume=20)

Channels
========

Pipettes can also be assigned a number of channels, either ``channel=1`` or ``channel=8``. If you do not specify, it will default to ``channel=1`` channel.

.. testcode:: pipettes

    pipette = instruments.Pipette(
        axis='b',
        name='my-p200-multichannel',
        max_volume=200,
        min_volume=20,
        channels=8)

Plunger Speeds
==============

The speeds at which the pipette will aspirate and dispense can be set through ``aspirate_speed`` and ``dispense_speed``. The values are in millimeters/minute, and default to ``aspirate_speed=300`` and ``dispense_speed=500``.

.. testcode:: pipettes

    pipeipette = instruments.Pipette(
        axis='b',
        name='my-p200-multichannel',
        max_volume=200,
        min_volume=20,
        channels=8,
        aspirate_speed=200,
        dispense_speed=600)

.. testsetup:: robot

    from opentrons import robot, containers, instruments

    robot.reset()

    plate = containers.load('96-flat', 'B1', 'my-plate')
    tiprack = containers.load('tiprack-200ul', 'A1', 'my-rack')

    pipette = instruments.Pipette(axis='b', max_volume=200, name='my-pipette')

**********************

**************
Tip Handling
**************

When we handle liquids with a pipette, we are constantly exchanging old, used tips for new ones to prevent cross-contamination between our wells. To help with this constant need, we describe in this section a few methods for getting new tips, and removing tips from a pipette.

**********************

.. testsetup:: tips

    from opentrons import containers, instruments, robot

    robot.reset()

    trash = containers.load('point', 'D2')
    tiprack = containers.load('tiprack-200ul', 'B1')

    pipette = instruments.Pipette(axis='a')

This section demonstrates the options available for controlling tips

.. testcode:: tips
    
    '''
    Examples in this section expect the following
    '''
    from opentrons import containers, instruments

    trash = containers.load('point', 'D2')
    tiprack = containers.load('tiprack-200ul', 'B1')

    pipette = instruments.Pipette(axis='a')

Pick Up Tip
===========

Before any liquid handling can be done, your pipette must have a tip on it. The command ``pick_up_tip()`` will move the pipette over to the specified tip, the press down into it to create a vacuum seal. The below example picks up the tip at location ``'A1'``.

.. testcode:: tips

    pipette.pick_up_tip(tiprack.wells('A1'))

Drop Tip
===========

Once finished with a tip, the pipette will autonomously remove the tip when we call ``drop_tip()``. We can specify where to drop the tip by passing in a location. The below example drops the tip back at its originating location on the tip rack.

.. testcode:: tips

    pipette.drop_tip(tiprack.wells('A1'))

Instead of returning a tip to the tip rack, we can also drop it in a trash container.

.. testcode:: tips

    pipette.pick_up_tip(tiprack.wells('A2'))
    pipette.drop_tip(trash)

Return Tip
===========

When we need to return the tip to its originating location on the tip rack, we can simply call ``return_tip()``. The example below will automatically return the tip to ``'A3'`` on the tip rack.

.. testcode:: tips

    pipette.pick_up_tip(tiprack.wells('A3'))
    pipette.return_tip()

**********************

.. testsetup:: tipsiterating

    from opentrons import containers, instruments, robot

    robot.reset()

    trash = containers.load('point', 'D2')
    tip_rack_1 = containers.load('tiprack-200ul', 'B1')
    tip_rack_2 = containers.load('tiprack-200ul', 'B2')

    pipette = instruments.Pipette(
        axis='b',
        tip_racks=[tip_rack_1, tip_rack_2],
        trash_container=trash
    )

Tips Iterating
==============

Automatically iterate through tips and drop tip in trash by attaching containers to a pipette

.. testcode:: tipsiterating
    
    '''
    Examples in this section expect the following
    '''
    from opentrons import containers, instruments

    trash = containers.load('point', 'D2')
    tip_rack_1 = containers.load('tiprack-200ul', 'B1')
    tip_rack_2 = containers.load('tiprack-200ul', 'B2')

Attach Tip Rack to Pipette
--------------------------

Tip racks and trash containers can be "attached" to a pipette when the pipette is created. This give the pipette the ability to automatically iterate through tips, and to automatically send the tip to the trash container.

Trash containers can be attached with the option ``trash_container=TRASH_CONTAINER``.

Multiple tip racks are can be attached with the option ``tip_racks=[RACK_1, RACK_2, etc... ]``.

.. testcode:: tipsiterating

    pipette = instruments.Pipette(
        axis='b',
        tip_racks=[tip_rack_1, tip_rack_2],
        trash_container=trash
    )

.. note::

    The ``tip_racks=`` option expects us to give it a Python list, containing each tip rack we want to attach. If we are only attaching one tip rack, then the list will have a length of one, like the following:

    ``tip_racks=[tiprack]``

Iterating Through Tips
----------------------

Now that we have two tip racks attached to the pipette, we can automatically step through each tip whenever we call ``pick_up_tip()``. We then have the option to either ``return_tip()`` to the tip rack, or we can ``drop_tip()`` to remove the tip in the attached trash container.

.. testcode:: tipsiterating

    pipette.pick_up_tip()  # picks up tip_rack_1:A1
    pipette.return_tip()
    pipette.pick_up_tip()  # picks up tip_rack_1:A2
    pipette.drop_tip()     # automatically drops in trash

    # use loop to pick up tips tip_rack_1:A3 through tip_rack_2:H12
    for i in range(94 + 96):
        pipette.pick_up_tip()
        pipette.return_tip()

If we try to ``pick_up_tip()`` again when all the tips have been used, the opentrons API will show you an error.

.. note::

    If you run the cell above, and then uncomment and run the cell below, you will get an error because the pipette is out of tips.

.. testcode:: tipsiterating

    # this will raise an exception if run after the previous code block
    # pipette.pick_up_tip()

Select Starting Tip
-------------------

Calls to ``pick_up_tip()`` will by default start at the attached tip rack's ``'A1'`` location. If you however want to start automatic tip iterating at a different tip, you can use ``start_at_tip()``.

.. testcode:: tipsiterating

    pipette.reset()

    pipette.start_at_tip(tip_rack_1['C3'])
    pipette.pick_up_tip()  # pick up C3 from "tip_rack_1"
    pipette.return_tip()

Get Current Tip
---------------

Get the source location of the pipette's current tip by calling ``current_tip()``. If the tip was from the ``'A1'`` position on our tip rack, ``current_tip()`` will return that position.

.. testcode:: tipsiterating

    print(pipette.current_tip())  # is holding no tip

    pipette.pick_up_tip()
    print(pipette.current_tip())  # is holding the next available tip

    pipette.return_tip()
    print(pipette.current_tip())  # is holding no tip

will print out...

.. testoutput:: tipsiterating

    None
    <Well D3>
    None

**********************

****************
Liquid Control
****************

This is the fun section, where we get to move things around and pipette! This section describes the ``Pipette`` object's many liquid-handling commands, as well as how to move the ``robot``.

**********************

.. testsetup:: liquid

    from opentrons import containers, instruments, robot

    robot.reset()

    plate = containers.load('96-flat', 'B1')
    pipette = instruments.Pipette(axis='b', max_volume=200)

.. testcode:: liquid
    
    '''
    Examples in this section expect the following
    '''
    from opentrons import containers, instruments

    plate = containers.load('96-flat', 'B1')
    pipette = instruments.Pipette(axis='b', max_volume=200)

Aspirate
========

To aspirate is to pull liquid up into the pipette's tip. When calling aspirate on a pipette, we can specify how many micoliters, and at which location, to draw liquid from:

.. testcode:: liquid

    pipette.aspirate(50, plate.wells('A1'))  # aspirate 50uL from plate:A1

Now our pipette's tip is holding 50uL.

We can also simply specify how many microliters to aspirate, and not mention a location. The pipette in this circumstance will aspirate from it's current location (which we previously set as ``plate.wells('A1'))``.

.. testcode:: liquid

    pipette.aspirate(50)                     # aspirate 50uL from current position

Now our pipette's tip is holding 100uL.

We can also specify only the location to aspirate from. If we do not tell the pipette how many micoliters to aspirate, it will by default fill up the remaining volume in it's tip. In this example, since we already have 100uL in the tip, the pipette will aspirate another 100uL

.. testcode:: liquid

    pipette.aspirate(plate.wells('A2'))      # aspirate until pipette fills from plate:A2

Dispense
========

To dispense is to push out liquid from the pipette's tip. It's usage in the opentrons API is nearly identical to ``aspirate()``, in that you can specify microliters and location, only microliters, or only a location:

.. testcode:: liquid

    pipette.dispense(50, plate.wells('B1')) # dispense 50uL to plate:B1
    pipette.dispense(50)                    # dispense 50uL to current position
    pipette.dispense(plate.wells('B2'))     # dispense until pipette empties to plate:B2

That final dispense without specifying a micoliter amount will dispense all remaining liquids in the tip to ``plate.wells('B2')``, and now our pipette is empty.

Blow Out
========

To blow out is to push an extra amount of air through the pipette's tip, so as to make sure that any remaining droplets are expelled.

When calling ``blow_out()`` on a pipette, we have the option to specify a location to blow out the remaining liquid. If no location is specified, the pipette will blow out from it's current position.

.. testcode:: liquid

    pipette.blow_out()                  # blow out over current location
    pipette.blow_out(plate.wells('B3')) # blow out over current plate:B3

Touch Tip
=========

To touch tip is to move the pipette's currently attached tip to the edges of a well, for the purpose of knocking off any droplets that might be hanging from the tip.

When calling ``touch_tip()`` on a pipette, we have the option to specify a location where the tip will touch the inner walls. If no location is specified, the pipette will touch tip inside it's current location.

.. testcode:: liquid

    pipette.touch_tip()                  # touch tip within current location
    pipette.touch_tip(-2)                # touch tip 2mm below the top of the current location
    pipette.touch_tip(plate.wells('B1')) # touch tip within plate:B1

Mix
===

Mixing is simply performing a series of ``aspirate()`` and ``dispense()`` commands in a row on a single location. However, instead of having to write those commands out every time, the opentrons API allows you to simply say ``mix()``.

The mix command takes three arguments: ``mix(repetitions, volume, location)``

.. testcode:: liquid

    pipette.mix(4, 100, plate.wells('A2'))   # mix 4 times, 100uL, in plate:A2
    pipette.mix(3, 50)                       # mix 3 times, 50uL, in current location
    pipette.mix(2)                           # mix 2 times, pipette's max volume, in current location

Air Gap
=======

Some liquids need an extra amount of air in the pipette's tip to prevent it from sliding out. A call to ``air_gap()`` with a microliter amount will aspirate that much air into the tip.

.. testcode:: liquid

    pipette.aspirate(100, plate.wells('B4'))
    pipette.air_gap(20)

**********************

.. testsetup:: moving

    from opentrons import robot, containers, instruments

    robot.reset()

    tiprack = containers.load('tiprack-200ul', 'A1')
    plate = containers.load('96-flat', 'B1')

    pipette = instruments.Pipette(axis='b')

******
Moving
******

Demonstrates the different ways to control the movement of the opentrons liquid handler during a protocol run.

.. testcode:: moving
    
    '''
    Examples in this section expect the following
    '''
    from opentrons import containers, instruments, robot

    tiprack = containers.load('tiprack-200ul', 'A1')
    plate = containers.load('96-flat', 'B1')

    pipette = instruments.Pipette(axis='b')

Move To
=======

Pipette's are able to ``move_to()`` any location on the deck.

For example, we can move to the first tip in our tip rack:

.. testcode:: moving

    pipette.move_to(tiprack.wells('A1'))

You can also specify at what height you would like the robot to move to inside of a location using ``top()`` and ``bottom()`` methods on that location.

.. testcode:: moving

    pipette.move_to(plate.wells('A1').bottom())  # move to the bottom of well A1
    pipette.move_to(plate.wells('A1').top())     # move to the top of well A1
    pipette.move_to(plate.wells('A1').bottom(2)) # move to 2mm above the bottom of well A1
    pipette.move_to(plate.wells('A1').top(-2))   # move to 2mm below the top of well A1

The above commands will cause the robot's head to first move upwards, then over to above the target location, then finally downwards until the target location is reached. If instead you would like the robot to mive in a straight line to the target location, you can set the movement strategy to ``'direct'``.

.. testcode:: moving

    pipette.move_to(plate.wells('A1'), strategy='direct')

.. note::
    
    Moving with ``strategy='direct'`` will run the risk of colliding with things on your deck. Be very careful when using the option.

Usually the ``strategy='direct'`` option is useful when moving inside of a well. Take a look at the below sequence of movements, which first move the head to a well, and use 'direct' movements inside that well, then finally move on to a different well.

.. testcode:: moving

    pipette.move_to(plate.wells('A1'))
    pipette.move_to(plate.wells('A1').bottom(1), strategy='direct')
    pipette.move_to(plate.wells('A1').top(-2), strategy='direct')
    pipette.move_to(plate.wells('A1'))

Delay
=====

To have your protocol pause for any given number of minutes or seconds, simply call ``delay()`` on your pipette. The value passed into ``delay()`` is the number of minutes or seconds the robot will wait until moving on to the next commands.

.. testcode:: moving

    pipette.delay(seconds=2)             # pause for 2 seconds
    pipette.delay(minutes=5)             # pause for 5 minutes
    pipette.delay(minutes=5, seconds=2)  # pause for 5 minutes and 2 seconds

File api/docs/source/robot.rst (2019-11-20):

.. _robot:

.. testsetup:: robot

    from opentrons import containers, instruments, robot
    from opentrons.instruments import pipette as _pipette

    robot.reset()

    plate = robot.add_container('96-flat', 'B1', 'my-plate')

    tiprack = robot.add_container('tiprack-200ul', 'A1', 'my-rack')

    pipette = _pipette.Pipette(robot, axis='b', max_volume=200, name='my-pipette')

###################
Advanced Control
###################

.. note::

    The below features are designed for advanced users who wish to use the opentrons API in their own Python environment (ie Jupyter). This page is not relevant for users only using the opentrons App, because the features described below will not be accessible.

The robot module can be thought of as the parent for all aspects of the opentrons API. All containers, instruments, and protocol commands are added to and controlled by robot.

.. testcode:: robot

    '''
    Examples in this section require the following
    '''
    from opentrons import robot, containers, instruments

    plate = containers.load('96-flat', 'B1', 'my-plate')
    tiprack = containers.load('tiprack-200ul', 'A1', 'my-rack')

    pipette = instruments.Pipette(axis='b', max_volume=200, name='my-pipette')

Head Speed
==========

The maximum speed of the robot's head can be set using ``robot.head_speed()``. The value we set the speed to is in millimeters-per-second (mm/sec).

.. testcode:: robot

    robot.head_speed(5000)

.. note::

    Setting the head speed to above ``6000 mm/sec`` may cause your robot to "skip", which means the motors will lose their grip and make a loud vibrating noise. We recommend you try out different speed values on your robot, and see what works and what doesn't.

Homing
======

You can `home` the robot by calling ``home()``. You can also specify axes. The robot will home immdediately when this call is made.

.. testcode:: robot

    robot.home()           # home the robot on all axis
    robot.home('z')        # home the Z axis only

Commands
========

When commands are called on a pipette, they are recorded on the ``robot`` in the order they are called. You can see all past executed commands by calling ``robot.commands()``, which returns a `Python list`__.

__ https://docs.python.org/3.5/tutorial/datastructures.html#more-on-lists

.. testcode:: robot
    
    pipette.pick_up_tip(tiprack.wells('A1'))
    pipette.drop_tip(tiprack.wells('A1'))

    for c in robot.commands():
        print(c)

will print out...

.. testoutput:: robot
    :options: -ELLIPSIS, +NORMALIZE_WHITESPACE

    Picking up tip from <Deck><Slot A1><Container my-rack><Well A1>
    Drop_tip at <Deck><Slot A1><Container my-rack><Well A1>

Clear Commands
==============

We can erase the robot command history by calling ``robot.clear_commands()``. Any previously created instruments and containers will still be inside robot, but the commands history is erased.

.. testcode:: robot
    
    robot.clear_commands()
    pipette.pick_up_tip(tiprack['A1'])
    print('There is', len(robot.commands()), 'command')

    robot.clear_commands()
    print('There are now', len(robot.commands()), 'commands')

will print out...

.. testoutput:: robot
    :options: -ELLIPSIS, +NORMALIZE_WHITESPACE

    There is 1 command
    There are now 0 commands

Comment
=======

You can add a custom message to the list of command descriptions you see when running ``robot.commands()``. This command is ``robot.comment()``, and it allows you to print out any information you want at the point in your protocol

.. testcode:: robot
    
    robot.clear_commands()

    pipette.pick_up_tip(tiprack['A1'])
    robot.comment("Hello, just picked up tip A1")

    pipette.pick_up_tip(tiprack['A1'])
    robot.comment("Goodbye, just dropped tip A1")

    for c in robot.commands():
        print(c)

will print out...

.. testoutput:: robot
    :options: -ELLIPSIS, +NORMALIZE_WHITESPACE

    Picking up tip from <Deck><Slot A1><Container my-rack><Well A1>
    Hello, just picked up tip A1
    Picking up tip from <Deck><Slot A1><Container my-rack><Well A1>
    Goodbye, just dropped tip A1

Get Containers
==============

When containers are loaded, they are automatically added to the ``robot``. You can see all currently held containers by calling ``robot.get_containers()``, which returns a `Python list`__.

__ https://docs.python.org/3.5/tutorial/datastructures.html#more-on-lists

.. testcode:: robot
    
    for name, container in robot.get_containers():
        print(name, container.get_type())

will print out...

.. testoutput:: robot
    :options: -ELLIPSIS, +NORMALIZE_WHITESPACE

    my-plate 96-flat
    my-rack tiprack-200ul

Get Instruments
===============

When instruments are created, they are automatically added to the ``robot``. You can see all currently held instruments by calling ``robot.get_instruments()``, which returns a `Python list`__.

__ https://docs.python.org/3.5/tutorial/datastructures.html#more-on-lists

.. testcode:: robot
    
    for axis, pipette in robot.get_instruments():
        print(pipette.name, axis)

will print out...

.. testoutput:: robot
    :options: -ELLIPSIS, +NORMALIZE_WHITESPACE

    my-pipette B

Reset
=====

Calling ``robot.reset()`` will remove everything from the robot. Any previously added containers, pipettes, or commands will be erased.

.. testcode:: robot
    
    robot.reset()
    print(robot.get_containers())
    print(robot.get_instruments())
    print(robot.commands())

will print out...

.. testoutput:: robot
    :options: -ELLIPSIS, +NORMALIZE_WHITESPACE

    []
    []
    []

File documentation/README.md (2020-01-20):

## OpenWorkstation

The OpenWorkstation project provides an open source and modular concept to enable life science automation. The OpenWorkstation API and the assembly line inspired approach is built on top of the [Opentrons](https://opentrons.com/) platform.

<p align="center">
</p>

## Getting started

The documentation is divided into the following sections:

 * [Concept](concept.md) for general information
 * [Pre-requisites and installation](installation.md) describes what you will need to install the OpenWorkstation API
 * [Programming](programming.md) provides detailed instructions on writing scripts to operate the modules
 * [Development plan](documentation/dev_plan.md) outlines future work packages

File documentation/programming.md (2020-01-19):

The programming section will be updated within the next weeks to include more details about the code and general organization. If you have any questions, please do no hesitate to [get in touch](mailto:s.eggert@qut.edu.au) to discuss potential applications.

# Programming

The OpenWorkstation API is a simple Python framework designed to allow the operation of hardware modules.

## How it’s Organized
Protocol scripts generally contain the following sections:

Imports
Commands
Module-specific Commands
Protocol script

#### Import

Always include the OpenWorkstation API within your file.
```
pip3 install openworkstation
```

Currently, specific commands for a single module are saved in a separate module file. For example, the positions for the transport module are saved in the `moduleTransport.py` file. These module-specific have to be imported into the main `protocol.py` file. General commands, such as connect to USB port and homing, are defined in a separate `commands.py` file.

```
from commands import *
from modulePipetting import *
from moduleCrosslinker import *
from moduleStorage import *
from moduleTransportation import *
```

#### Connect to USB port(s)

The command `connect()` will connect to board to the USB port(s) which are defined in the `commands.py` file.

```
robot2USB  = '/dev/ttyACM1'
```

#### Homing
The command `home()` will start with the homing process for the defined axis.

```
def home_all():
    robot2._driver.send_command('G28.2 Y Z')
    robot2._driver.send_command('G28.2 A')
    robot2._driver.send_command('G28.2 B')
    robot2._driver.send_command('G28.2 X')
    robot2._driver.send_command('G90')
```

#### Move to defined positions
Basic commands are written in the [Gcode language](https://en.wikipedia.org/wiki/G-code) to enable customization of movements and make it accessible to anyone with basic programming skills.

##### Switching between relative and absolute coordinates

Switch to absolute coordinates
```
robot2._driver.send_command('G90')
```
Switch to relative coordinates
```
robot2._driver.send_command('G91')
```

##### Define movement speed

Define speed in mm/min
```
robot2._driver.send_command('G0 F1000')
```

##### Define movement steps

```
robot2._driver.send_command('G0 X5 Y100 A88')
robot2._driver.send_command('G0 X0 Y150 A33')
```

#### Advanced control

If specific protocol blocks or general functionalities are repeated from time to time, parameters can be defined at the beginning and called in a function.

```
# definitions of module positions for the moduleTransport
transportposition['modulePipetting']  = 'G0 X481 Y5 Z5 A4 B5 F2000'
transportposition['moduleCrosslinker']  = 'G0 X170 Y5 Z5 A4 B5 F2000'
transportposition['moduleStorage']  = 'G0 X21.3 Y5 Z5 A4 B5 F2000'
# definition of crosslinker parameters for the moduleCrosslinker
# used to initiate photo-induced polymerization of hydrogels
lightON  = 'M106'
lightOFF  = 'M107'

# define function
def crosslinking1min():
    #absolute positioning
    robot2._driver.send_command('G90')
    # move plate to crosslinker module
    robot2._driver.send_command(transportposition['moduleCrosslinker'])
    # specifiy intensity
    robot2._driver.send_command(intensity_P1)
    # LEDs on
    robot2._driver.send_command(lightON)
    # duration
    sleep(60)
    # LEDs off
    robot2._driver.send_command(lightOFF)
    # move plate to pipetting module
    robot2._driver.send_command(transportposition['modulePipetting'])

# call function in protocol
crosslinking1min()

```

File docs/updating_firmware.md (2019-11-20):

#Updating Firmware

The motorcontroller inside all opentrons liquid handlers (called Smoothieboard or just Smoothie) will need it's firmware updated if you are planning to use the opentrons API and accompanying 2.0 app. The process is simple, and can be done from your computer in under a minute.

To summarize, there are two files on your Smoothie that must be replaced; `FIRMWARE.CUR` and `config`. 

##Step 1
###Download Files

[Download the zipped files from here](https://github.com/opentrons/smoothie-config/archive/1.2.0.zip). After downloading, unpack the zip file to view its contents.

##Step 2
###Open the Smoothie's Drive

Select Config File

Power on and plug in your opentrons liquid handler, and make sure you do not have the app open. You will notice the Smoothieboard shows up on the computer as a Mass Storage Device, like an external hard drive or flash drive.

Select Config File

Open the Smoothie's storage device to see it's `FIRMWARE.CUR` and `config` files. There might be other files there, but the two you need to worry about are `FIRMWARE.CUR` and `config`, because these are what we will be replacing.

##Step 3
###Copy Over `firmware.bin`

From the folder you downloaded from GitHub, find the `firmware.bin` file.

Select Config File

Drag `firmware.bin` to the Smoothie's drive. Your drive should now look like the following:

Select Config File

##Step 4
###Select Your opentrons Model Config

opentrons [come in three models](https://opentrons.com/robots), the Standard, Pro, and Hood. Each model requires a unique "config" file to go along with it. Find the config file that matches your robot (the folders are named after each model).

Select Config File

Drag the `config` file from the correct folder onto the Smoothie's drive. You will be overwriting the old `config` file, so your computer may ask if you would like to proceed with replacing it.

Select Config File

##Step 5
###Restart

Unmount the Smoothie's driver from your computer, and power cycle the robot. When the Smoothieboard powers on, it will read the `firmware.bin` file, then save it as `FIRMWARE.CUR`. It will then read the new `config` file, and your liquid handler now has updated firmware.

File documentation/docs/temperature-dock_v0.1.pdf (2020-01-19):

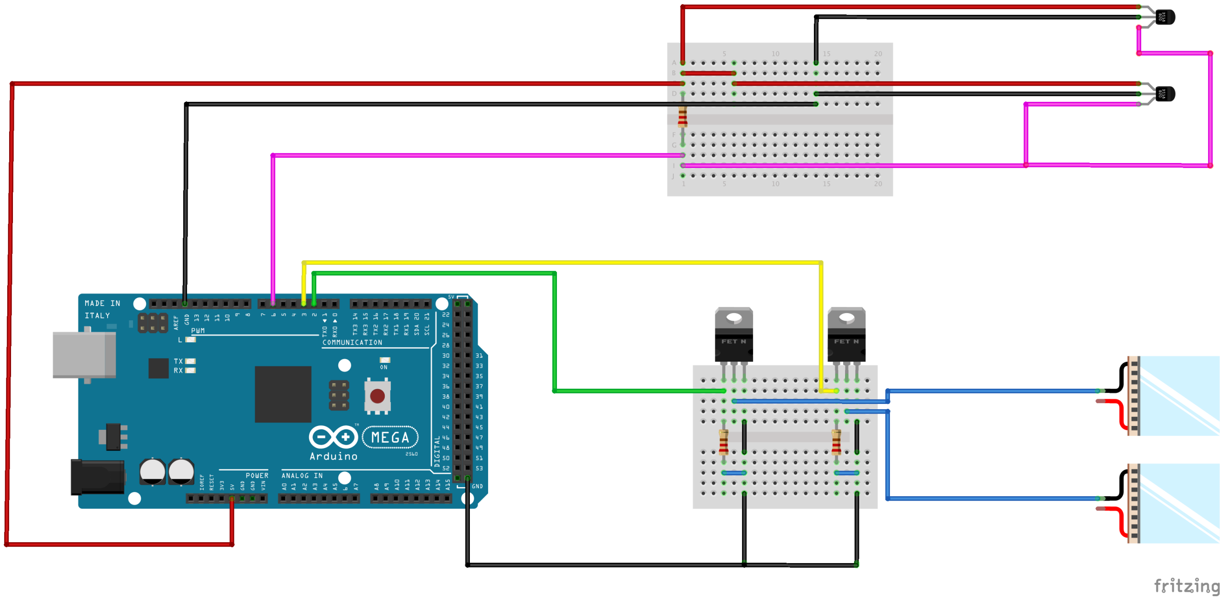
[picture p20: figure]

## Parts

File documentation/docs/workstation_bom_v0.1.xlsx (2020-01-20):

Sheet: bom_modules
module | designator | component | manufacturer/supplier | part-number | number of item(s) | length in m | cost per unit (or per metre) | price in USD | link | comment
computational module
 | raspberry pi | Raspberry Pi 3 Model B+ | Adafruit Industries (NY, USA) | 3775 | 1 |  | 35.00 | 35.00 | https://www.adafruit.com/product/3775
 | raspberry pi power supply | Raspberry Pi Power Supply | Adafruit Industries (NY, USA) | 1995 | 1 |  | 7.50 | 7.50 | https://www.adafruit.com/product/1995
 | microSD card | MicroSD card with NOOBS | Adafruit Industries (NY, USA) | 3259 | 1 |  | 9.95 | 9.95 | https://www.adafruit.com/product/3259
 | arduino | Arduino Mega | SparkFun Electronics, Inc (CO, USA) | DEV-11061 | 1 |  | 38.95 | 38.95 | https://www.sparkfun.com/products/11061
 | mosfet | MOSFET-FQP30N06L | SparkFun Electronics, Inc (CO, USA) | COM-10213 | 2 |  | 0.95 | 1.90 | https://www.sparkfun.com/products/10213
 | breadboard | breadboard, 170 pin (max 5A rating) | Newark element14 (IL, USA) | 71Y9231 | 2 |  | 1.53 | 3.06 | https://www.newark.com/pro-signal/psg-bb-170w/breadboard-solderless-plastic/dp/71Y9231
control box and electronics
 | smoothieboard | Smoothieboard, 5XC-R, version1.1, voltage reg 1A | Uberclock, LL (OR, USA) | smoothie_5x | 1 |  | 189.00 | 189.00 | https://shop.uberclock.com/products/smoothieboard
 | fan | fan, 80mm, 12V | Newark element14 (IL, USA) | 29M8108 | 2 |  | 11.39 | 22.78 | https://www.newark.com/nmb-technologies/3110kl-04w-b30-d00/axial-fan-80mm-12vdc-170ma/dp/29M8108
 | fan grid | fan guard for 80x80mm fan | Newark element14 (IL, USA) | 56P2990 | 4 |  | 1.07 | 4.28 | https://www.newark.com/multicomp/mc32794/finger-guard/dp/56P2990?st=fan%20grid%2080
 | power supply | power supply 12V/29A (Meanwell) set | OpenBuilds (NJ, USA) | 511-Set | 1 |  | 59.99 | 59.99 | https://openbuildspartstore.com/12v-29a-meanwell-power-supply-bundle/
 | 2-core cable | 2-core cable, screened, 0.5mm(2), 50m | Newark element14 (IL, USA) | 50AC7152 | 1 |  | 26.90 | 26.90 | https://www.newark.com/pro-power/pp001555/shld-flex-cable-2cond-0-5mm2-50m/dp/50AC7152
 | 4-core cable | 4-core cable, screened, 0.5mm(2), 50m | Newark element14 (IL, USA) | 50AC7160 | 1 |  | 50.60 | 50.60 | https://www.newark.com/pro-power/pp001563/shld-flex-cable-4cond-0-5mm2-50m/dp/50AC7160
 | connectors: 2pins | xtension connectors 2pin | OpenBuilds (NJ, USA) | 2525-Set | 6 |  | 1.49 | 8.94 | https://openbuildspartstore.com/xtension-connectors/ | for each end stop connection (5x), LED connection (1x)
 | connectors: 4pins | xtension connectors 4pin | OpenBuilds (NJ, USA) | 2525-Set | 5 |  | 3.49 | 17.45 | https://openbuildspartstore.com/xtension-connectors/ | for each stepper motor connection: 5x
 | acrylic plates | acrylic plates 10mm, black | Mulford Plastics PTY LTD (QLD, Australia) | ASTARIGLAS-GP-10mm-black | 1 |  |  | 0.00 | https://www.mulfordplastics.com.au/products/acrylic-cast/
 | acrylic plates | acrylic plates 10mm, white | Mulford Plastics PTY LTD (QLD, Australia) | ASTARIGLAS-GP-10mm-white | 1 |  |  | 0.00 | https://www.mulfordplastics.com.au/products/acrylic-cast/
 | acrylic plates | acrylic plates 6mm, white | Mulford Plastics PTY LTD (QLD, Australia) | ASTARIGLAS-GP-6mm-white | 1 |  |  | 0.00 | https://www.mulfordplastics.com.au/products/acrylic-cast/
frame
 | aluminium profile | profile 30x30 (slot 8mm) | GAP Engineering PTY LTD (QLD, Australia) | 084.107.002 |  | 4.84 | 10.50 | 50.82 | https://aluminiumprofile.com.au/product/profile-30x30-8mm-slot/
 | clamping angle | clamping angle 25x40 | GAP Engineering PTY LTD (QLD, Australia) | 084.305.002 | 12 |  | 2.45 | 29.40 | https://aluminiumprofile.com.au/product/clamping-angle-25x40/
 | nuts | nut M8 - slot 8 (pack of 25) | GAP Engineering PTY LTD (QLD, Australia) | 084.302.037 | 1 |  | 17.00 | 17.00 | https://aluminiumprofile.com.au/product/nut-m8-ss-slot-8/
 | bolts | bolt M8x16mm - slot 8 (pack of 25) | GAP Engineering PTY LTD (QLD, Australia) | 084.301.002 | 1 |  | 4.00 | 4.00 | https://aluminiumprofile.com.au/product/bolt-m8x16/
 | cable management | drag chain cable carrier: 1m | OpenBuilds (NJ, USA) | 2450 | 2 |  | 15.99 | 47.97 | https://openbuildspartstore.com/drag-chain-cable-carrier/
 | mounting bracket | cable drag chain mounting bracket | Makerstore (Australia) | BRAC-CDC | 6 |  | 3.70 | 22.00 | https://www.makerstore.com.au/product/cable-drag-chain-mounting-bracket/
transport module
 | linear actuator | 1000mm C-Beam® XLarge Linear Actuator Bundle (w NEMA23) | OpenBuilds (NJ, USA) | 2495-Bundle | 1 |  | 174.99 | 174.99 | https://openbuildspartstore.com/c-beam-xlarge-linear-actuator-bundle/
 | limit switch | Xtension Limit Switch Kit | OpenBuilds (NJ, USA) | 2805-Kit | 1 |  | 4.99 | 4.99 | https://openbuildspartstore.com/xtension-limit-switch-kit/
 | nuts | nut M5 - slot 8 (pack of 25) | GAP Engineering PTY LTD (QLD, Australia) | 084.302.002 | 1 |  | 3.55 | 3.55 | https://aluminiumprofile.com.au/product/nut-m5-slot-8/
 | nuts | tee nuts (M5) (pack of 10) | OpenBuilds (NJ, USA) | 536-Pack | 1 |  | 2.99 | 2.99 | https://openbuildspartstore.com/tee-nuts-m5-10-pack/
 | screw | M5x15mm (pack of 10) | OpenBuilds (NJ, USA) | 922-pack | 2 |  | 1.59 | 3.18 | https://openbuildspartstore.com/low-profile-screws-m5-10-pack/
 | connectors | black corner brackets | OpenBuilds (NJ, USA) | 540 | 8 |  | 2.99 | 23.92 | https://openbuildspartstore.com/black-angle-corner-connector/
 | cable management | drag chain cable carrier (10 x 15mm): 1m | OpenBuilds (NJ, USA) | 2450 | 3 |  | 15.99 | 47.97 | https://openbuildspartstore.com/drag-chain-cable-carrier/
pipetting module
 | pipetting robot | OT-One S Hood | Opentrons Laboratories Inc (NY, USA) | OT-One S Hood | 1 |  | 4000.00 | 4000.00 | https://shop.opentrons.com/products/ot-hood
 | temperature probe | Waterproof DS18B20 Digital temperature sensor | Adafruit Industries (NY, USA) | 381 | 2 |  | 9.95 | 19.90 | https://www.adafruit.com/product/381
 | peltier | peltier thermo-electric cooler module (12V, 5A) | Adafruit Industries (NY, USA) | 1330 | 4 |  | 11.95 | 47.80 | https://www.adafruit.com/product/1330
 | 2-core cable | 2-core cable, screened, 0.5mm(2), 50m | Newark element14 (IL, USA) | 50AC7152 | 0 |  | 26.90 | 0.00 | https://www.newark.com/pro-power/pp001555/shld-flex-cable-2cond-0-5mm2-50m/dp/50AC7152
 | 4-core cable | 4-core cable, screened, 0.5mm(2), 50m | Newark element14 (IL, USA) | 50AC7160 | 0 |  | 50.60 | 0.00 | https://www.newark.com/pro-power/pp001563/shld-flex-cable-4cond-0-5mm2-50m/dp/50AC7160
 | connectors: 2pins | xtension connectors 2pin | OpenBuilds (NJ, USA) | 2525-Set | 0 |  | 1.49 | 0.00 | https://openbuildspartstore.com/xtension-connectors/
 | connectors: 4pins | xtension connectors 4pin | OpenBuilds (NJ, USA) | 2525-Set | 0 |  | 3.49 | 0.00 | https://openbuildspartstore.com/xtension-connectors/
 | acrylic plates | acrylic plates 10mm, white | Mulford Plastics PTY LTD (QLD, Australia) | ASTARIGLAS-GP-10mm-white | 0 |  |  | 0.00 | https://www.mulfordplastics.com.au/products/acrylic-cast/
crosslinker module
 | linear actuator | 500mm C-Beam® Linear Actuator Bundle (w NEMA23) | OpenBuilds (NJ, USA) | 995-Bundle | 1 |  | 144.99 | 144.99 | https://openbuildspartstore.com/c-beam-linear-actuator-bundle/
 | linear actuator | 250mm C-Beam® Linear Actuator Bundle (w NEMA23) | OpenBuilds (NJ, USA) | 995-Bundle | 1 |  | 126.99 | 126.99 | https://openbuildspartstore.com/c-beam-linear-actuator-bundle/
 | limit switch | Xtension Limit Switch Kit | OpenBuilds (NJ, USA) | 2805-Kit | 2 |  | 4.99 | 9.98 | https://openbuildspartstore.com/xtension-limit-switch-kit/
 | aluminium profile | profile 30x30 (slot 8mm) | GAP Engineering PTY LTD (QLD, Australia) | 084.107.002 |  | 4.26 | 10.50 | 44.73 | https://aluminiumprofile.com.au/product/profile-30x30-8mm-slot/
 | aluminium profile | profile 20x20 (V slot): 500mm | OpenBuilds (NJ, USA) | VSlot20x20LinearRail | 3 |  | 5.49 | 16.47 | https://openbuildspartstore.com/v-slot-20x20-linear-rail/
 | clamping angle | clamping angle 25x40 | GAP Engineering PTY LTD (QLD, Australia) | 084.305.002 | 4 |  | 2.45 | 9.80 | https://aluminiumprofile.com.au/product/clamping-angle-25x40/
 | nuts | nut M5 - slot 8 (pack of 25) | GAP Engineering PTY LTD (QLD, Australia) | 084.302.002 | 1 |  | 3.55 | 3.55 | https://aluminiumprofile.com.au/product/nut-m5-slot-8/
 | bolts | bolt M5x16mm - slot 8 (pack of 25) | GAP Engineering PTY LTD (QLD, Australia) | 084.301.009 | 1 |  | 2.88 | 2.88 | https://aluminiumprofile.com.au/product-category/connectors/connectors-bolts/
 | connectors | black corner brackets | OpenBuilds (NJ, USA) | 540 | 12 |  | 2.99 | 35.88 | https://openbuildspartstore.com/black-angle-corner-connector/
 | nuts | tee nuts (M5) (pack of 10) | OpenBuilds (NJ, USA) | 536-Pack | 3 |  | 2.99 | 8.97 | https://openbuildspartstore.com/tee-nuts-m5-10-pack/
 | screws | M5x8mm (pack of 10) | OpenBuilds (NJ, USA) | 946-pack | 3 |  | 1.39 | 4.17 | https://openbuildspartstore.com/low-profile-screws-m5-10-pack/ | total number of screws depends on usage of connectors
 | screws | M5x10mm (pack of 10) | OpenBuilds (NJ, USA) | 878-pack | 3 |  | 1.49 | 4.47 | https://openbuildspartstore.com/low-profile-screws-m5-10-pack/
 | screws | M5x15mm (pack of 10) | OpenBuilds (NJ, USA) | 922-pack | 3 |  | 1.59 | 4.77 | https://openbuildspartstore.com/low-profile-screws-m5-10-pack/
 | screws | M5x20mm (pack of 10) | OpenBuilds (NJ, USA) | 750-pack | 3 |  | 1.69 | 5.07 | https://openbuildspartstore.com/low-profile-screws-m5-10-pack/
 | plates | 90 degree joining plate | OpenBuilds (NJ, USA) | 610 | 8 |  | 4.99 | 39.92 | https://openbuildspartstore.com/90-degree-joining-plate/
 | spacer | aluminium spacer: 6mm | OpenBuilds (NJ, USA) | 90-Pack | 4 |  | 2.99 | 11.96 | https://openbuildspartstore.com/aluminum-spacers-10-pack/ | height depends on application: distance between slider and well plate
 | LED strip lights | LED strip light: 399nm (reel, 5m) | Flexfire LEDs, Inc.(CA, USA) | CB-UV-12V-16FT | 1 |  | 175.00 | 175.00 | https://www.flexfireleds.com/colorbright-uv-purple-led-strip-light-by-the-foot/
 | cable management | drag chain cable carrier (10 x 15mm): 0.5m | OpenBuilds (NJ, USA) | 2450 | 3 |  | 7.99 | 23.97 | https://openbuildspartstore.com/drag-chain-cable-carrier/
 | 2-core cable | 2-core cable, screened, 0.5mm(2), 50m | Newark element14 (IL, USA) | 50AC7152 | 0 |  | 26.90 | 0.00 | https://www.newark.com/pro-power/pp001555/shld-flex-cable-2cond-0-5mm2-50m/dp/50AC7152
 | 4-core cable | 4-core cable, screened, 0.5mm(2), 50m | Newark element14 (IL, USA) | 50AC7160 | 0 |  | 50.60 | 0.00 | https://www.newark.com/pro-power/pp001563/shld-flex-cable-4cond-0-5mm2-50m/dp/50AC7160
 | connectors: 2pins | xtension connectors 2pin | OpenBuilds (NJ, USA) | 2525-Set | 0 |  | 1.49 | 0.00 | https://openbuildspartstore.com/xtension-connectors/
 | connectors: 4pins | xtension connectors 4pin | OpenBuilds (NJ, USA) | 2525-Set | 0 |  | 3.49 | 0.00 | https://openbuildspartstore.com/xtension-connectors/
 | acrylic plates | acrylic plates 10mm, black | Mulford Plastics PTY LTD (QLD, Australia) | ASTARIGLAS-GP-10mm-black | 0 |  |  | 0.00 | https://www.mulfordplastics.com.au/products/acrylic-cast/
storage module
 | linear actuator | 500mm C-Beam® Linear Actuator Bundle (w NEMA23) | OpenBuilds (NJ, USA) | 995-Bundle | 1 |  | 144.99 | 144.99 | https://openbuildspartstore.com/c-beam-linear-actuator-bundle/
 | linear actuator | 250mm Belt & Pinion Actuator Bundle (w NEMA23) | OpenBuilds (NJ, USA) | 2565-Bundle | 1 |  | 109.99 | 109.99 | https://openbuildspartstore.com/nema-23-belt-pinion-actuator-bundle/
 | limit switch | Xtension Limit Switch Kit | OpenBuilds (NJ, USA) | 2805-Kit | 2 |  | 4.99 | 9.98 | https://openbuildspartstore.com/xtension-limit-switch-kit/
 | aluminium profile | profile 30x30 (slot 8mm) | GAP Engineering PTY LTD (QLD, Australia) | 084.107.002 |  | 5.266 | 10.50 | 0.00 | https://aluminiumprofile.com.au/product/profile-30x30-8mm-slot/
 | aluminium profile | profile 20x20 (V slot): 500mm | OpenBuilds (NJ, USA) | VSlot20x20LinearRail | 4 |  | 5.49 | 21.96 | https://openbuildspartstore.com/v-slot-20x20-linear-rail/
 | aluminium profile | profile 20x20 (V slot): 250mm (to be cut) | OpenBuilds (NJ, USA) | VSlot20x20LinearRail | 8 |  | 3.29 | 26.32 | https://openbuildspartstore.com/v-slot-20x20-linear-rail/
 | aluminium profile | profile 20x40 (V slot): 250mm (to be cut) | OpenBuilds (NJ, USA) | VSlot20x40LinearRail | 1 |  | 3.99 | 3.99 | https://openbuildspartstore.com/v-slot-20x40-linear-rail/
 | clamping angle | clamping angle 25x40 | GAP Engineering PTY LTD (QLD, Australia) | 084.305.002 | 4 |  | 2.45 | 9.80 | https://aluminiumprofile.com.au/product/clamping-angle-25x40/
 | nuts | nut M5 - slot 8 (pack of 25) | GAP Engineering PTY LTD (QLD, Australia) | 084.302.002 | 1 |  | 3.55 | 3.55 | https://aluminiumprofile.com.au/product/nut-m5-slot-8/
 | bolts | bolt M5x16mm - slot 8 (pack of 25) | GAP Engineering PTY LTD (QLD, Australia) | 084.301.009 | 1 |  | 2.88 | 2.88 | https://aluminiumprofile.com.au/product-category/connectors/connectors-bolts/
 | nuts | tee nuts (M5) (pack of 10) | OpenBuilds (NJ, USA) | 536-Pack | 3 |  | 2.99 | 8.97 | https://openbuildspartstore.com/tee-nuts-m5-10-pack/
 | connectors | black corner brackets | OpenBuilds (NJ, USA) | 540 | 12 |  | 2.99 | 35.88 | https://openbuildspartstore.com/black-angle-corner-connector/
 | screws | M5x8mm (pack of 10) | OpenBuilds (NJ, USA) | 946-pack | 3 |  | 1.39 | 4.17 | https://openbuildspartstore.com/low-profile-screws-m5-10-pack/
 | screws | M5x10mm (pack of 10) | OpenBuilds (NJ, USA) | 878-pack | 3 |  | 1.49 | 4.47 | https://openbuildspartstore.com/low-profile-screws-m5-10-pack/
 | screws | M5x15mm (pack of 10) | OpenBuilds (NJ, USA) | 922-pack | 3 |  | 1.59 | 4.77 | https://openbuildspartstore.com/low-profile-screws-m5-10-pack/
 | screws | M5x20mm (pack of 10) | OpenBuilds (NJ, USA) | 750-pack | 3 |  | 1.69 | 5.07 | https://openbuildspartstore.com/low-profile-screws-m5-10-pack/
 | screws | M5x25mm (pack of 10) | OpenBuilds (NJ, USA) | 20-pack | 1 |  | 1.79 | 1.79 | https://openbuildspartstore.com/low-profile-screws-m5-10-pack/
 | plates | 90 degree joining plate | OpenBuilds (NJ, USA) | 610 | 12 |  | 4.99 | 59.88 | https://openbuildspartstore.com/90-degree-joining-plate/
 | spacer | aluminium spacer: 20mm | OpenBuilds (NJ, USA) | 65-Pack | 4 |  | 2.99 | 11.96 | https://openbuildspartstore.com/aluminum-spacers-10-pack/
 | vacuum generator | vacuum ejector | Schmalz (Glatten, Germany) | 10.02.01.00565 | 1 |  | 38.62 | 38.62 | https://www.schmalz.com/en/10.02.01.00565
 | cups | bellows suction cups (oval): SPOB1 60x20 | Schmalz (Glatten, Germany) | 10.01.06.03511 | 2 |  | 37.50 | 75.00 | https://www.schmalz.com/en/10.01.06.03511
 | hose | hose, VSL 8-6 PU, external diameter D=8 mm, internal diameter d=6 mm | Schmalz (Glatten, Germany) | 10.07.09.00003 |  | 10 | 4.76 | 0.00 | https://www.schmalz.com/en/10.07.09.00003
 | connection plug | screw plug connection, straight | Schmalz (Glatten, Germany) | 10.08.02.00206 | 2 |  | 4.47 | 8.94 | https://www.schmalz.com/en/10.08.02.00206
 | connection plug | t-connection | Schmalz (Glatten, Germany) | 10.09.02.00022 | 1 |  | 16.43 | 16.43 | https://www.schmalz.com/en/10.09.02.00022
 | valve | 3/2 pneumatic control valve solenoid, G1/8, 12V | RS Components PTY LTD (NSW, Australia) | 797-5093 | 1 |  | 42.00 | 42.00 | https://au.rs-online.com/web/p/pneumatic-solenoid-pilot-operated-control-valves/7975093/
 | adapter | pneumatic straight threaded-to-tube adapter, G 1/8 male, push In 6 mm | RS Components PTY LTD (NSW, Australia) | 812-049 | 2 |  | 4.20 | 8.40 | https://au.rs-online.com/web/p/pneumatic-straight-threaded-to-tube-adaptors/0812049/
 | cable management | drag chain cable carrier (10 x 15mm): 0.5m | OpenBuilds (NJ, USA) | 2450 | 3 |  | 7.99 | 23.97 | https://openbuildspartstore.com/drag-chain-cable-carrier/
 | 2-core cable | 2-core cable, screened, 0.5mm(2), 50m | Newark element14 (IL, USA) | 50AC7152 | 0 |  | 26.90 | 0.00 | https://www.newark.com/pro-power/pp001555/shld-flex-cable-2cond-0-5mm2-50m/dp/50AC7152
 | 4-core cable | 4-core cable, screened, 0.5mm(2), 50m | Newark element14 (IL, USA) | 50AC7160 | 0 |  | 50.60 | 0.00 | https://www.newark.com/pro-power/pp001563/shld-flex-cable-4cond-0-5mm2-50m/dp/50AC7160 | only 2m required; remaining 3m will be given to CM for future crosslinker boxes
 | connectors: 2pins | xtension connectors 2pin | OpenBuilds (NJ, USA) | 2525-Set | 0 |  | 1.49 | 0.00 | https://openbuildspartstore.com/xtension-connectors/
 | connectors: 4pins | xtension connectors 4pin | OpenBuilds (NJ, USA) | 2525-Set | 0 |  | 3.49 | 0.00 | https://openbuildspartstore.com/xtension-connectors/
 | acrylic plates | acrylic plates 10mm, white | Mulford Plastics PTY LTD (QLD, Australia) | ASTARIGLAS-GP-10mm-white | 0 |  |  | 0.00 | https://www.mulfordplastics.com.au/products/acrylic-cast/
 | acrylic plates | acrylic plates 6mm, white | Mulford Plastics PTY LTD (QLD, Australia) | ASTARIGLAS-GP-6mm-white | 0 |  |  | 0.00 | https://www.mulfordplastics.com.au/products/acrylic-cast/

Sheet: frame-summary
 | number of item | required length in m | cost per item (or per metre)
profile 30 x 30 mm
 |  | 14.006 | 16
profile 20 x 20 mm
 |  | 5.68 | 11.5
profile 20 x 40 mm
 |  | 0.15 | 17
profile cutting service
 | 54 |  | 3
accessories
clamping angles (25x40) | #REF! |  | 3.3
clamping angles (29x29) | #REF! |  | 3.3
clamping angles (13x22) | #REF! |  | 2.2
nut M6 - slot8 (pack of 25) | #REF! |  | 5.1
nut M5 - slot8 (pack of 25) | #REF! |  | 5.1
bolts M6 (pack of 25) | #REF! |  | 4.8
bolts M5 (pack of 25) | #REF! |  | 4.8

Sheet: frame-details
profile length in mm | frame | transportation module | crosslinker module | storage module | total number | length in mm | total length in mm
profile 30 x 30 mm (slot 8mm) |  |  |  |  |  |  |  | addition per cut, in mm | 10
53 |  |  |  | 2 | 2 | 106
60 |  |  |  |  | 0 | 0 |  | module | length, in mm | cuts | total length required, in mm | in m
90 |  |  |  |  | 0 | 0 |  | frame | 4760 | 8 | 4840 | 4.84
130 |  |  |  | 2 | 2 | 260 |  | crosslinker modules | 4140 | 12 | 4260 | 4.26
140 |  |  | 5 |  | 5 | 700 |  | storage module | 5106 | 16 | 5266 | 5.266
260 | 1 |  |  | 5 | 6 | 1560
400 | 3 |  | 3 | 3 | 9 | 3600
460 |  |  |  |  | 0 | 0
520 | 2 |  |  |  | 2 | 1040
560 |  |  | 4 | 4 | 8 | 4480
1130 | 2 |  |  |  | 2 | 2260
 |  |  |  |  |  |  | 14006
profile 20 x 20 mm (slot 6mm)
150 |  |  |  | 4 | 4 | 600
170 |  |  |  | 4 | 4 | 680
400 |  |  | 1 |  | 1 | 400
500 |  |  | 4 | 4 | 8 | 4000
 |  |  |  |  |  |  | 5680
profile 20 x 40 mm (slot 6mm)
150 |  |  |  | 1 | 1 | 150
 |  |  |  |  |  |  | 150

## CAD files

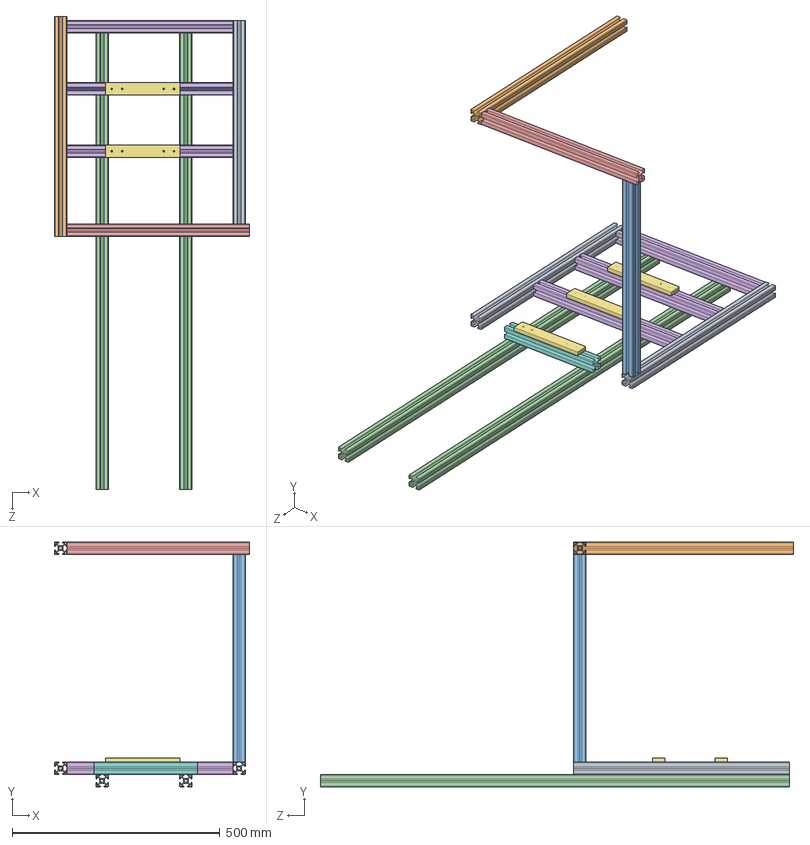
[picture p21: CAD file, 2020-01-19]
hardware/base-frame/frame_v1.3.SLDASM
470.0 x 590.0 x 1140.0 mm
profile_30x30mm_520mm x 2
Profile_30x30mm_1130mm x 2
Profile_30x30mm_400mm x 3
frame_spacer_v1.0 x 3
Profile_30x30mm_250mm

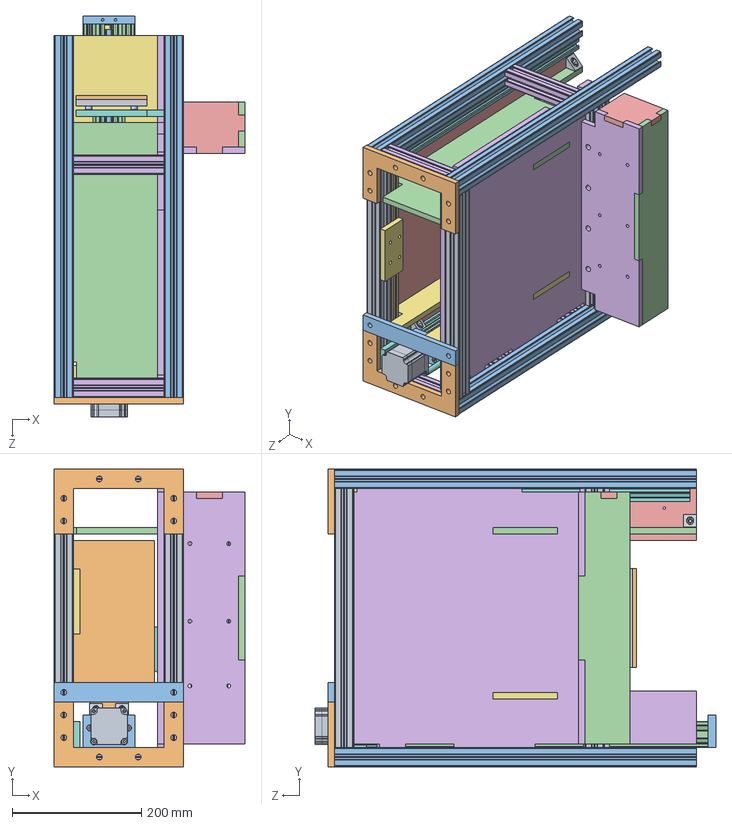
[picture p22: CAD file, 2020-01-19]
hardware/moduleCrosslinker/module_crosslinker_v1.8.SLDASM
295.0 x 460.0 x 620.0 mm
Profile_30x30mm_400mm x 3
led-panel_v1.4
profile_30x30mm_560mm x 4
m-cl_box-front_v1.4
m-cl_box-side-rigth_v1.4
m-cl_box-side-left_v1.4
m-cl_box-back_v1.3
m-cl_gradient-slider_v1.1
Low Profile Screw M5 x 32
Nylon Insert Lock Nut M5 x 12
C-Beam End Mount x 4
C-Beam 40x80x500 Linear Rail
Ball Bearing 8 x 16 x 5 x 4
Shim Washer 8mm x 4
Lock Collar 8mm x 4
Aluminum Spacer 40mm x 4
Nema 23 Stepper Motor x 2
Flexible Coupling 0.25in x 8mm x 2
8mm leadscrew 540mm
C-Beam Gantry Plate x 2
8mm Acme Nut Block x 2
Xtreme Mini V Wheel x 8
Ball Bearing 5 x 10 x 4.2 x 16
Precision Shim 8 x 5 x 1 x 16
Aluminum Spacer 6mm x 8
Mini Eccentric Spacer 6mm x 4
Aluminum Spacer 3mm x 4
C-Beam 40x80x250 Linear Rail
8mm leadscrew 290mm
Profile_30x30mm_140mm x 5
V-Slot 20x20x400 Linear Rail
V-Slot 20x20x500 Linear Rail x 2
Black Angle Corner Connector x 4
m-cl_profile-connector_v1.0 x 2
m-cl_connector_v1.0
m-cl_cover-side_v1.0
m-cl_cover-front_v1.0
m-cl_cover-top_v1.0
m-cl_profiles-20x30_connector_v1.0
m-cl_profiles-20x30_connector2_v1.0
m-cl_gradient-slider-spacer_v1.1
m-cl_gradient-slider-cover_v1.1

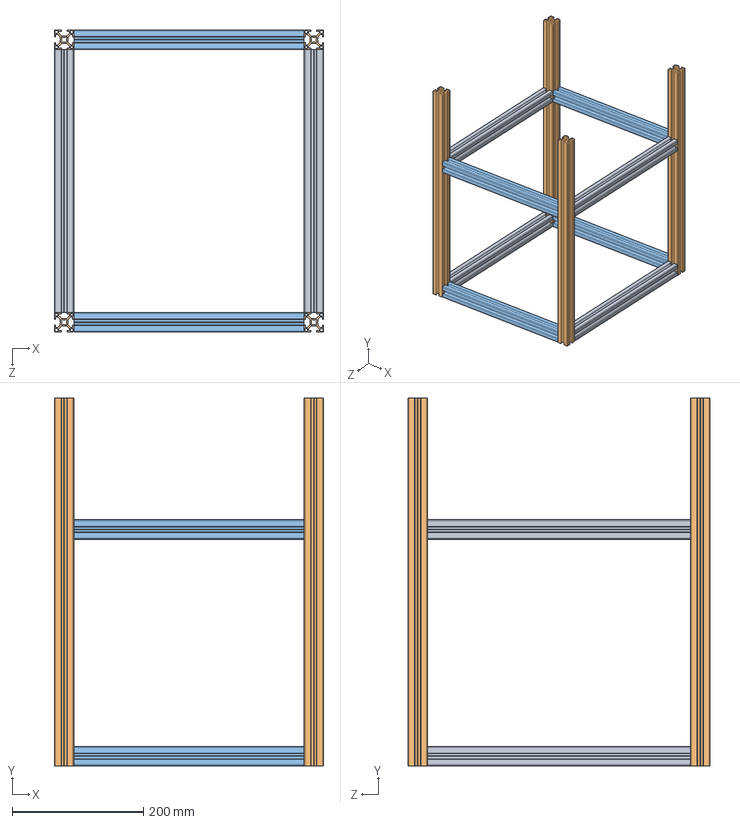
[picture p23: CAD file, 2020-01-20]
hardware/moduleFrame/module4_frame_v1.0.SLDASM
410.0 x 560.0 x 460.0 mm
Profile_30x30mm_400mm x 4
profile_30x30mm_560mm x 4
Profile_30x30mm_350mm x 4

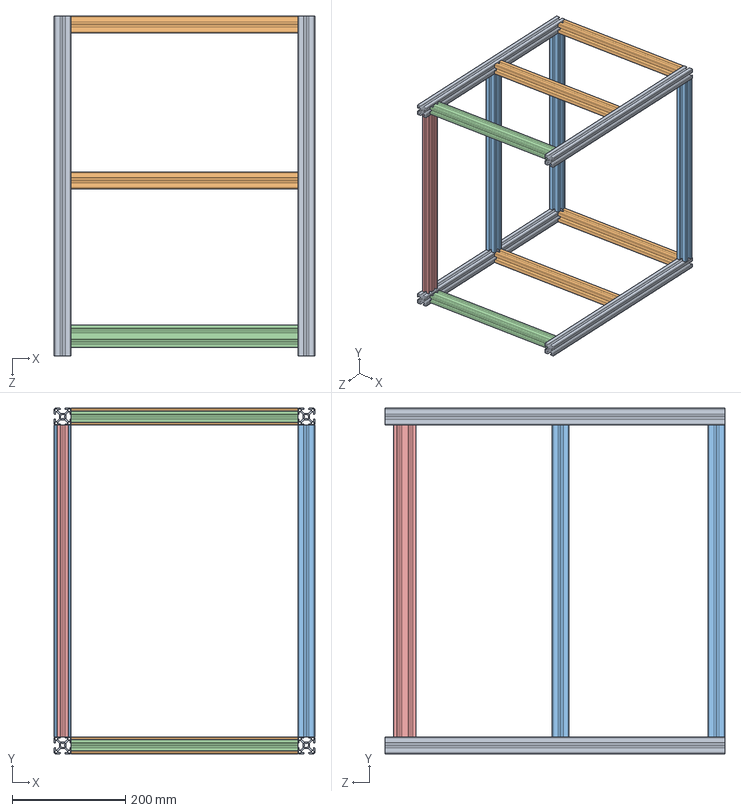
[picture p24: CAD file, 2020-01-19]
hardware/modulePipetting/frame_v0.1.SLDASM
460.0 x 610.0 x 600.0 mm
Profile_30x30mm_600mm x 4
Profile_30x30mm_400mm x 4
Profile_30x30mm_550mm x 3
V-Slot 20x40x400 Linear Rail x 2
V-Slot 20x40x550 Linear Rail

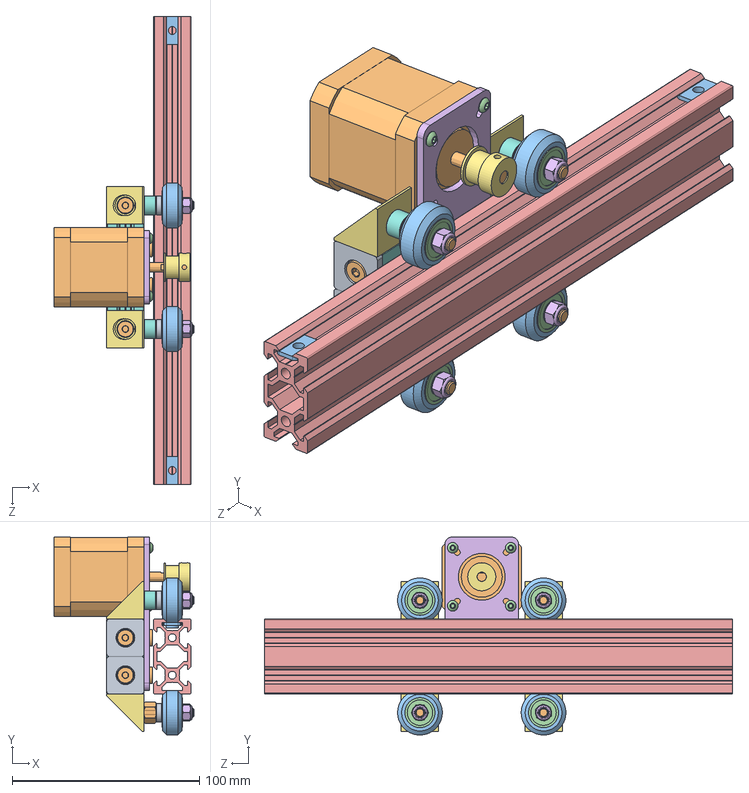
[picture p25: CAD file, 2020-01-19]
hardware/moduleStorage/Mini-V-Slot-Belt-Pinion-Actuator_250mm.SLDASM
74.5 x 105.7 x 250.0 mm
Double Tee Nut x 2
Low Profile Screw M5 x 16
Tee Nut x 6
Button Head Socket Cap Screw M3 x 4
V-Slot 20x40x250 Linear Rail
Motor Mount Plate Nema 17
Black Angle Corner Connector x 4
V-Slot 20x40x80 Linear Rail
End Cap x 4
Nema 17 Stepper Motor
Solid V Wheel x 4
Ball Bearing 5 x 16 x 5 x 8
Precision Shim 10 x 5 x 1 x 4
Nylon Insert Lock Nut M5 x 4
GT2 Timing Pulley 20 Tooth
Aluminum Spacer .25in x 2
Aluminum Spacer .125in x 4
Eccentric Spacer 0.25in x 2

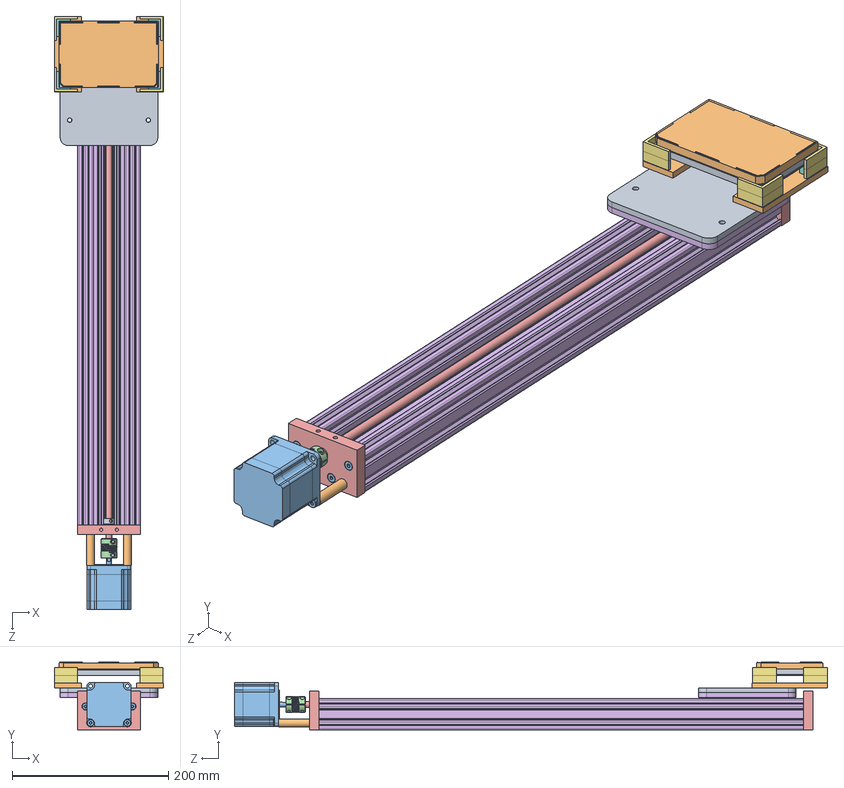
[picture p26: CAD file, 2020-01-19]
hardware/moduleTransport/module_transportation_v1.1.SLDASM
140.0 x 86.7 x 758.5 mm
Low Profile Screw M5 x 16
Nylon Insert Lock Nut M5 x 6
C-Beam End Mount x 2
C-Beam 40x80x620 Linear Rail
Ball Bearing 8 x 16 x 5 x 2
Shim Washer 8mm x 2
Lock Collar 8mm x 2
Aluminum Spacer 40mm x 2
Nema 23 Stepper Motor
Flexible Coupling 0.25in x 8mm
8mm leadscrew 660mm
8mm Acme Nut Block
Xtreme Mini V Wheel x 4
Ball Bearing 5 x 10 x 4.2 x 8
Precision Shim 8 x 5 x 1 x 8
Aluminum Spacer 6mm x 2
Mini Eccentric Spacer 6mm x 2
Aluminum Spacer 3mm x 2
C-Beam Gantry Plate XLarge
m-t_sidewalls_v1.1 x 2
m-t_spacer_v1.2
m-t_base-spacer_v1.0
m-t_base_v1.3

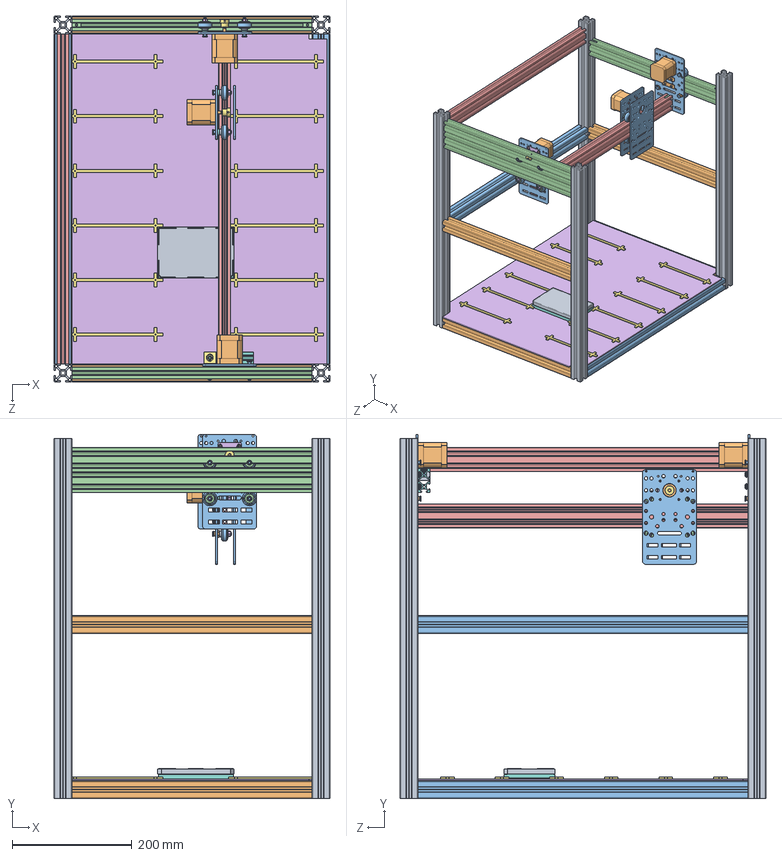
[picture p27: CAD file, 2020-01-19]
hardware/workstation/module_pipetting_v0.7.SLDASM
460.0 x 607.0 x 610.0 mm
Profile_30x30mm_600mm x 4
Profile_30x30mm_400mm x 4
Profile_30x30mm_550mm x 3
V-Slot 20x40x550 Linear Rail x 2
baseplate_v0.2
container-holder_v0.1 x 12
96 Well Plate Base
96 Well Plate Lid
Double Tee Nut x 6
Low Profile Screw M5 x 24
Button Head Socket Cap Screw M3 x 12
Tee Nut x 6
V-Slot 20x40x400 Linear Rail x 2
Motor Mount Plate Nema 17 x 3
Nema 17 Stepper Motor x 3
Solid V Wheel x 12
Ball Bearing 5 x 16 x 5 x 24
Precision Shim 10 x 5 x 1 x 12
Nylon Insert Lock Nut M5 x 12
GT2 Timing Pulley 20 Tooth x 3
Aluminum Spacer .25in x 6
Aluminum Spacer .125in x 12
Eccentric Spacer 0.25in x 6
1002_Motor_Mount_Plate x 4

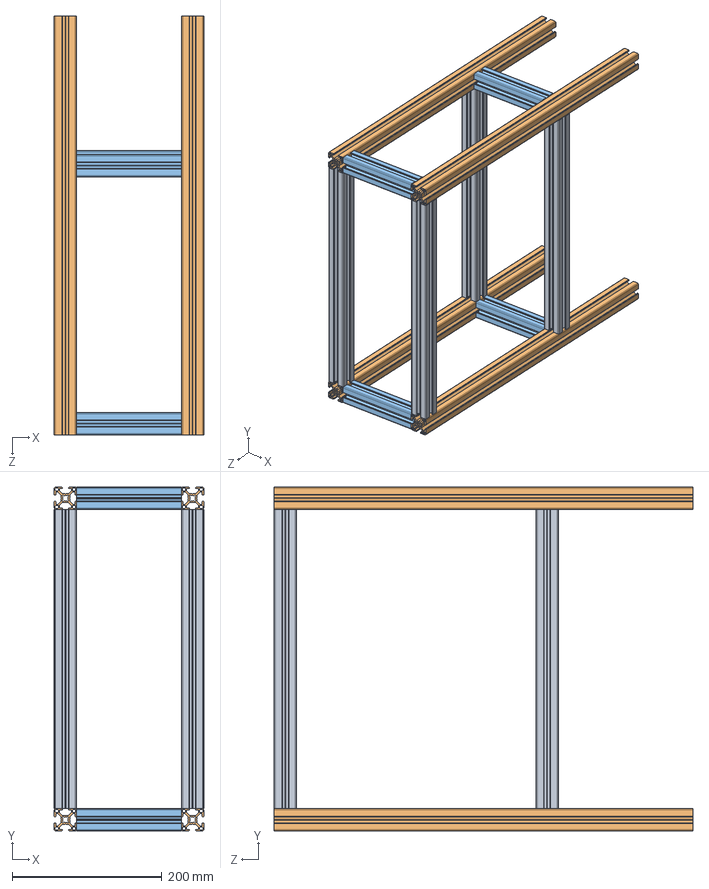
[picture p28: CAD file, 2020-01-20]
hardware/moduleFrame/module2_frame_v1.0.SLDASM
200.0 x 460.0 x 560.0 mm
Profile_30x30mm_400mm x 4
profile_30x30mm_560mm x 4
Profile_30x30mm_140mm x 4

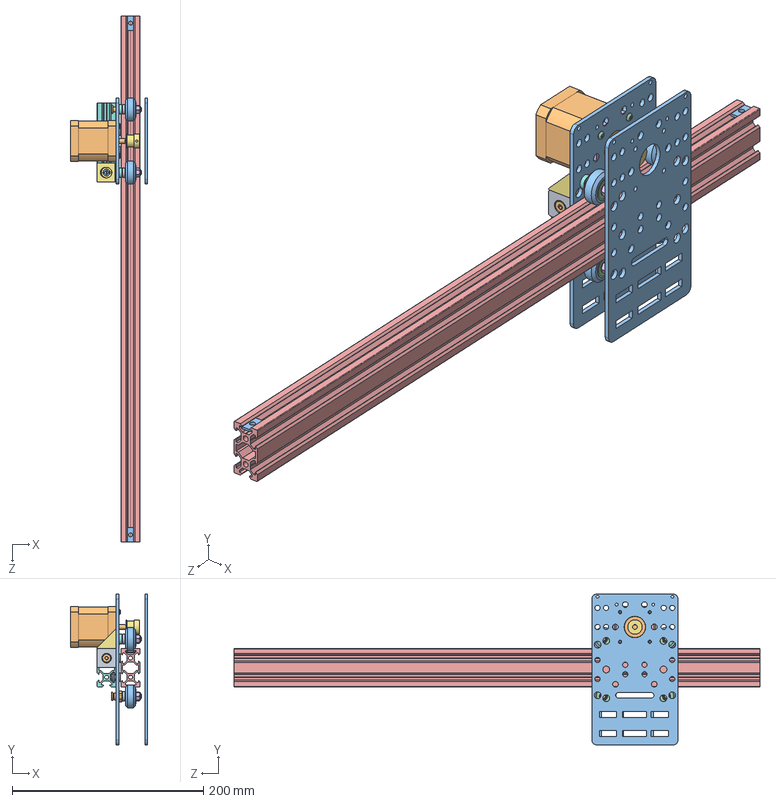
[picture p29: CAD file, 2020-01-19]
hardware/modulePipetting/Mini-V-Slot-Belt-Pinion-Actuator_550mm_v0.1.SLDASM
81.0 x 157.7 x 550.0 mm
Double Tee Nut x 2
Low Profile Screw M5 x 8
Button Head Socket Cap Screw M3 x 4
Tee Nut x 2
V-Slot 20x40x550 Linear Rail
Motor Mount Plate Nema 17
Nema 17 Stepper Motor
Solid V Wheel x 4
Ball Bearing 5 x 16 x 5 x 8
Precision Shim 10 x 5 x 1 x 4
Nylon Insert Lock Nut M5 x 4
GT2 Timing Pulley 20 Tooth
Aluminum Spacer .25in x 2
Aluminum Spacer .125in x 4
Eccentric Spacer 0.25in x 2
1002_Motor_Mount_Plate x 2

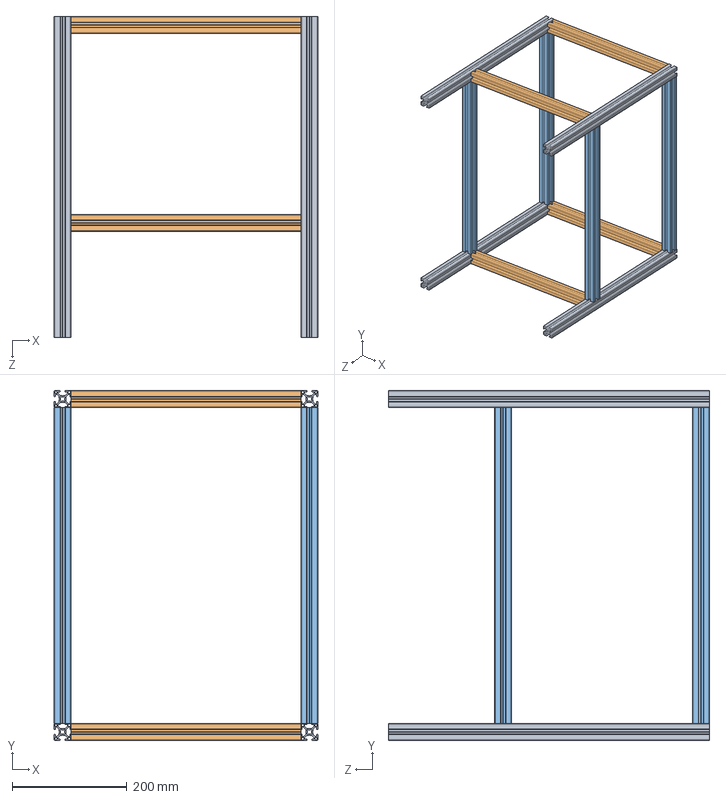
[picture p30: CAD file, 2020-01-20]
hardware/moduleFrame/module1_frame_v1.0.SLDASM
460.0 x 610.0 x 560.0 mm
profile_30x30mm_560mm x 4
Profile_30x30mm_400mm x 4
Profile_30x30mm_550mm x 4

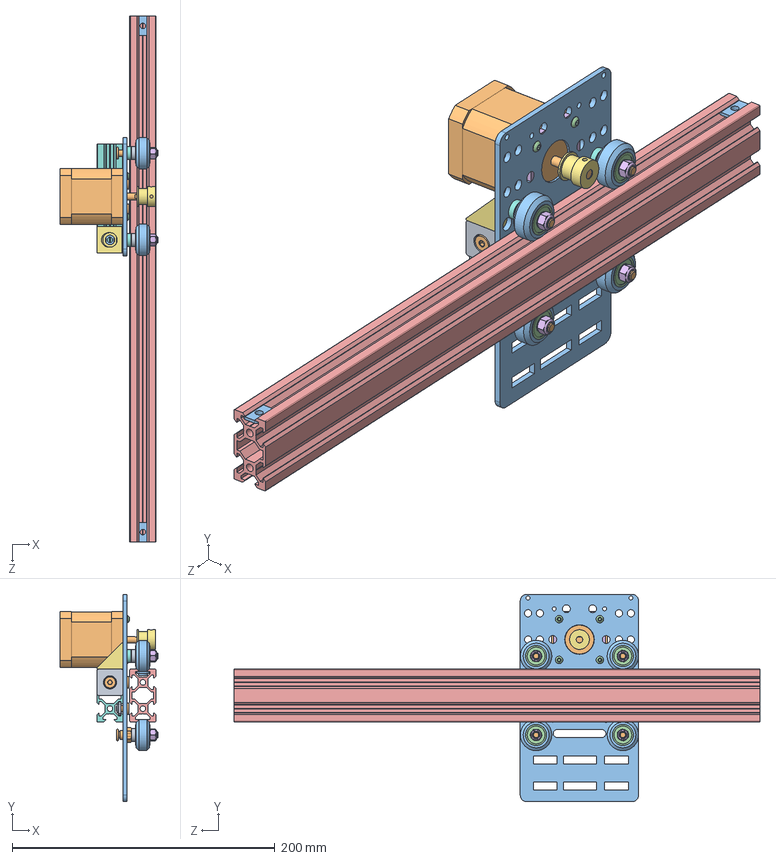
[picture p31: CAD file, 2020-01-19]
hardware/modulePipetting/Mini-V-Slot-Belt-Pinion-Actuator_400mm_v0.1.SLDASM
74.5 x 157.7 x 400.0 mm
Double Tee Nut x 2
Low Profile Screw M5 x 8
Button Head Socket Cap Screw M3 x 4
Tee Nut x 2
V-Slot 20x40x400 Linear Rail
Motor Mount Plate Nema 17
Nema 17 Stepper Motor
Solid V Wheel x 4
Ball Bearing 5 x 16 x 5 x 8
Precision Shim 10 x 5 x 1 x 4
Nylon Insert Lock Nut M5 x 4
GT2 Timing Pulley 20 Tooth
Aluminum Spacer .25in x 2
Aluminum Spacer .125in x 4
Eccentric Spacer 0.25in x 2
1002_Motor_Mount_Plate

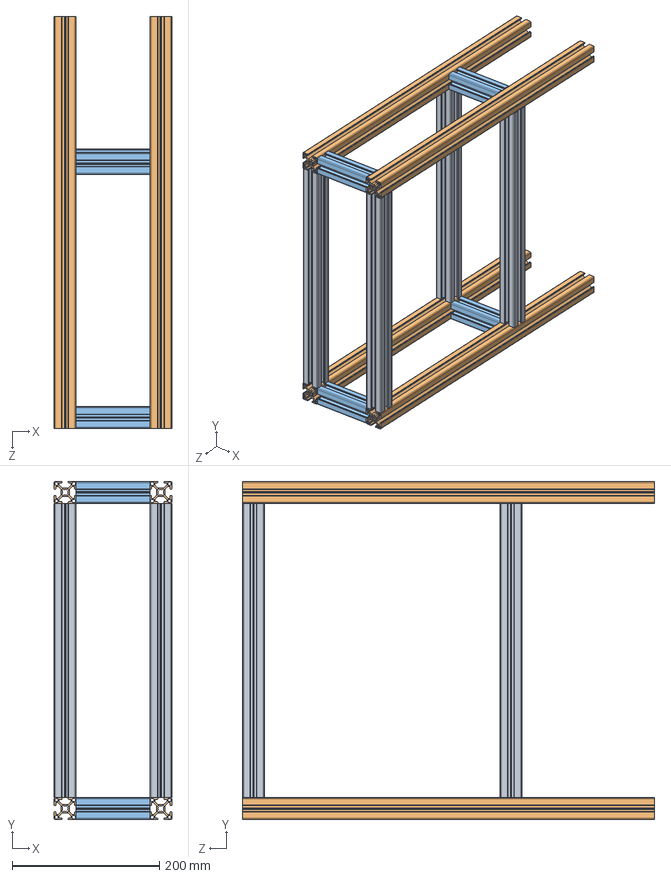
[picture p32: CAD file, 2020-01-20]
hardware/moduleFrame/module5_frame_v1.0.SLDASM
160.0 x 460.0 x 560.0 mm
Profile_30x30mm_400mm x 4
profile_30x30mm_560mm x 4
Profile_30x30mm_100mm x 4

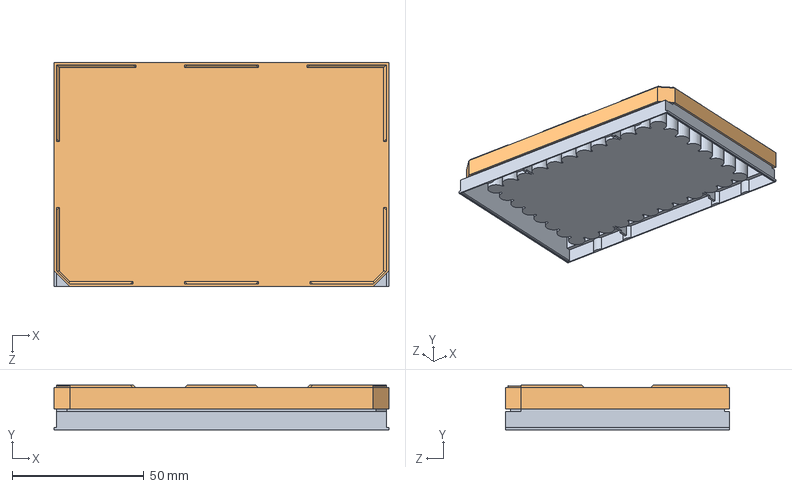
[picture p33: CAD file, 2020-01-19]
hardware/modulePipetting/96 Well Cell Culture Test Plate Assembly.SLDASM
127.0 x 17.0 x 85.0 mm
96 Well Plate Base
96 Well Plate Lid

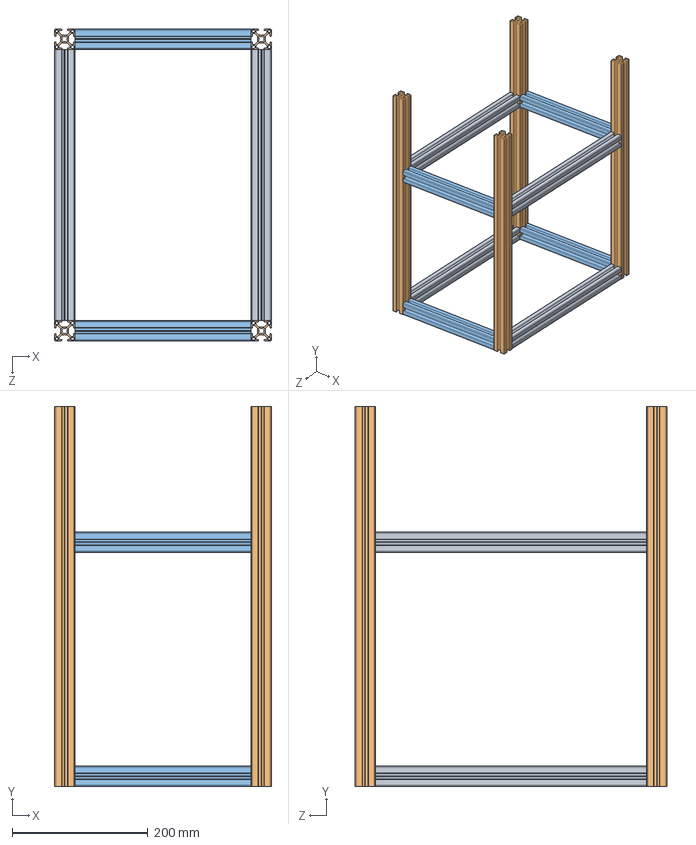
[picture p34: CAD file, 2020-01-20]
hardware/moduleFrame/module3_frame_v1.0.SLDASM
320.0 x 560.0 x 460.0 mm
Profile_30x30mm_400mm x 4
profile_30x30mm_560mm x 4
profile_30x30mm_260mm x 4

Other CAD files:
hardware/modulePipetting/Solid V Wheel assy.SLDASM
hardware/moduleFrame/module6_frame_v1.0.SLDASM
hardware/moduleFrame/module7_frame_v1.0.SLDASM
hardware/moduleFrame/module_frame_overview_v0.1.SLDASM
hardware/aluminium-profiles/30x30mm/profile-30x30mm_1000mm.SLDPRT
hardware/aluminium-profiles/30x30mm/profile-30x30mm_250mm.SLDPRT
hardware/base-frame/Profile_30x30mm_1130mm.SLDPRT
hardware/base-frame/Profile_30x30mm_250mm.SLDPRT
hardware/base-frame/Profile_30x30mm_400mm.SLDPRT
hardware/base-frame/Profile_30x30mm_440mm.SLDPRT
hardware/base-frame/Profile_30x30mm_500mm.SLDPRT
hardware/base-frame/frame_spacer_v1.0.SLDPRT
hardware/base-frame/profile_30x30mm_520mm.SLDPRT
hardware/base-frame/profile_30x30mm_530mm.SLDPRT
hardware/moduleCrosslinker/8mm Acme Nut Block.SLDPRT
hardware/moduleCrosslinker/8mm leadscrew 290mm.SLDPRT
hardware/moduleCrosslinker/8mm leadscrew 540mm.SLDPRT
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

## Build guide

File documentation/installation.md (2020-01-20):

# Pre-requisites and installation

The following instructions are written for a Raspberry Pi (RPi) single-board computer; however also Windows 8, 10 and macOS 10.12+ have been successfully used with the presented workstation:

#### Python version

Make sure that you have at least Python 3.5 on your system.

#### Update the system's package list

```
sudo apt-get update
```

#### Upgrade all the installed packages

```
sudo apt-get dist-upgrade
```

#### Restart the Raspberry Pi

```
sudo reboot
```

#### Install Python pip

```
sudo apt-get install python3-pip
```

#### Create a Python virtual environment

It is recommended to setup an [Python Virtual Environment](https://realpython.com/python-virtual-environments-a-primer/) to store all packages and dependencies in one place. By doing this, your current Opentrons API is not impacted by any changes.

Install the virtualenv tool
```
pip3 install virtualenv
```

Create a new virtual environment
```
python3 -m venv OpenWorkstation
```

Activate the Python virtual environment
```
source OpenWorkstation/bin/activate
```

#### Install OpenWorkstation API
```
pip3 install openworkstation
```

#### Install opentrons API

The opentrons API is only required, if the OT-1 or the OT-2 is used as the pipetting module.

For OT-1 API
```
pip3 install opentrons==2.5.2
```

For OT-2 API
```
pip3 install opentrons
```

The current version has been tested successfully with the OT-1 API and should be compatible with the OT-2 API.

#### Test successful API installation

```
python3
>>> import openworkstation
>>> import opentrons
```

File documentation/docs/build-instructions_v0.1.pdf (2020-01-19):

build_instructions_v0.1

## Step-by-Step Build Setup Guide

### Table of Contents

1 Base | 2
2 Transportation module | 2
3 Crosslinker module | 4
4 Storage module | 6
5 Electrical control box | 8

### 1 Base

The assembly process for the base is depicted in Figure 1.

Depending on the support (e.g. table, lab bench, biological safety cabinet, etc), select an appropriate solution to connect the workstation with the support. If the workstation is to be placed in a biological safety hood, keep the available height of the internal dimensions in mind.

Timing | 1 – 2 hours
Materials | 30x30mm aluminium profiles, screws (M5, M6), clamping angles, tee nuts for M5
and M6, laser cut parts (specifications are listed in the BOM)
Equipment | M5, M6 Allen key
Critical | cutting surface of aluminium profile should be straight
1| | Laser cut acrylic plates
2| | Position two aluminium profiles (30x30mm, 1540mm) next two each other
3| | Connect a grid base structure with four aluminium profiles (30x30mm, 400mm) to the base
with 29x29 clamping angles using M6x15 screws and M6 nuts

3| Attached spacer plates to the grid base structure using M5x15 screws and M5 nuts.

### 2 Transportation module

The assembly process for the transport module is depicted in Figure 1.

This module transports sample to the installed modules using a linear actuator and a sample holder. Depending on the overall length of the workstation, the length of the transportation module has to be selected to ensure that the sample can be transported to each module. The sample holder design can be optimized to the required experimental applications.

Timing | 1 day
Materials | linear actuators, M5 screws, corner brackets, tee nuts for M5, laser cut parts (specifications are listed in the BOM)
Equipment | M5 Allen key
Critical | cutting surface of aluminium profile should be straight

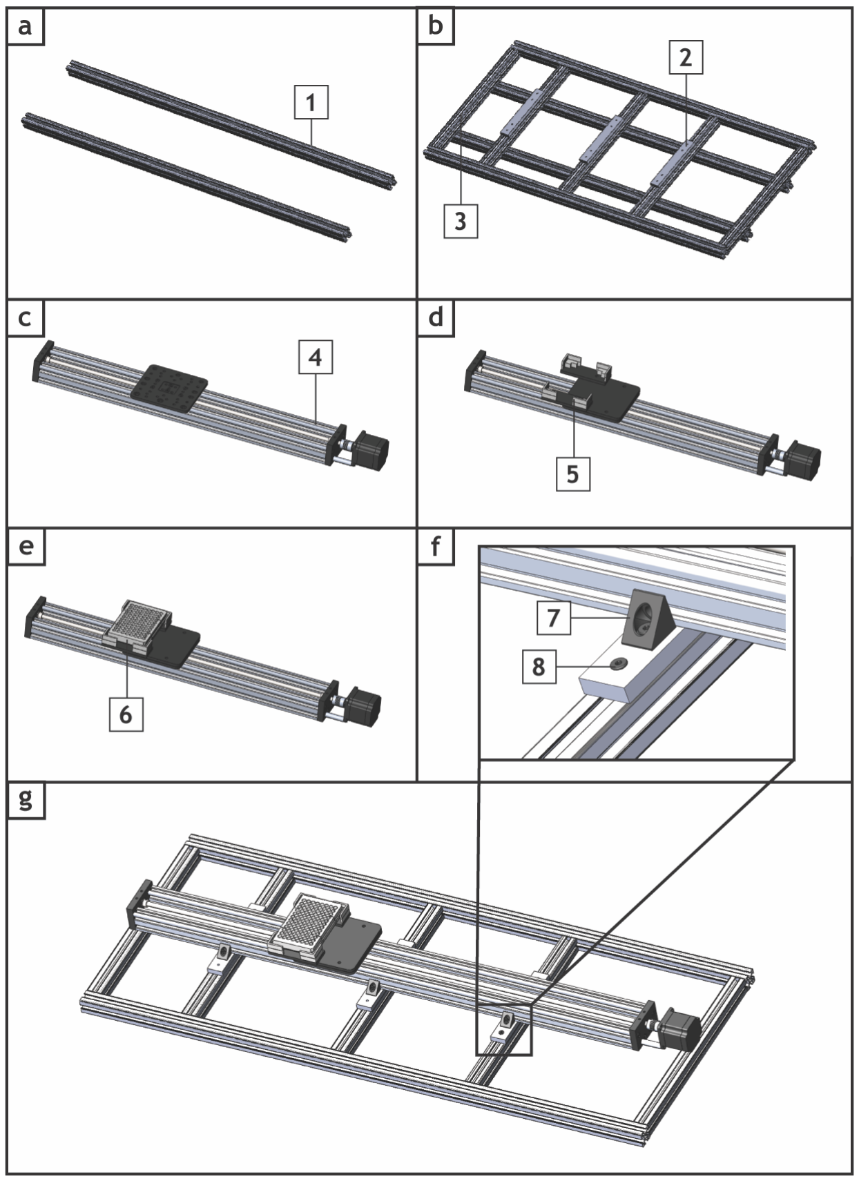
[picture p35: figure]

Figure 1: Assembly process for base (a,b), transport module (c-e), and connecting both (g). Parts: Two 30x30mm aluminium profiles (1), connecting struts (3) with spacer (2), linear stage (4) with holder (5) for well plate (6), and corner brackets (7) and screws (8).

1| | Laser cut acrylic plates as listed in the BOM
2| | Assemble the linear actuator (C-Beam Gantry Actuator) as instructed by OpenBuilds¹
3| | Assemble sample holder and attach to gantry plate using M5x15 screws
4| | Base und transportation module are connected using corner brackets.
5| | Y-direction of transportation module can be adjusted by positioning the plate spacers

### 3 Crosslinker module

The assembly process for the crosslinker module is depicted in Figure 2.

The crosslinker module provide photo-induced crosslinking and the ability to generate time gradients using a sliding mask. The LED panel provides a plug-and-play mode to enable fast modification and a customized solution.

Timing | 3 days
Materials | linear actuators for module as specified in BOM, 20x20mm and 30x30mm aluminium
profiles, screws (M3, M5, M6), clamping angles, tee nuts for M5 and M6, NEMA23 stepper motors, cable housing, laser cut parts
Equipment | M3, M5, M6 Allen key
Critical | cutting surface of aluminium profile should be straight
1| | Laser cut acrylic plates
2| | Assemble the two linear actuators as instructed by OpenBuilds²
3| | For the sliding mask, connect the sliding plates to the assembled 250mm linear actuator
using M5 screws

4| Attach enclosure to assembly using M5x15 screws and M5 tee nuts

1 https://www.youtube.com/watch?v=tLozVt_CjXQ 2 https://www.youtube.com/watch?v=tLozVt_CjXQ

5| | The module assembly starts by building the base frame using 30x30 mm profiles which are connected with 29x29 clamping angles using M6x15 screws and M6 nuts
6| | Attach right side wall to the base frame using M5x15 screw and M5 tee nuts
7| | Attach linear actuator to the back of the module, followed by putting in the back and front enclosure plate as well as the LED panel. The LED panel is attached to the gantry plate via two corner brackets
8| | Attach end stop holder at the top. Height and position can be customized/optimized later
9| | Connect left enclosure plate and missing profile
10| | Finish crosslinker assembly by attaching the sliding mask on the left side

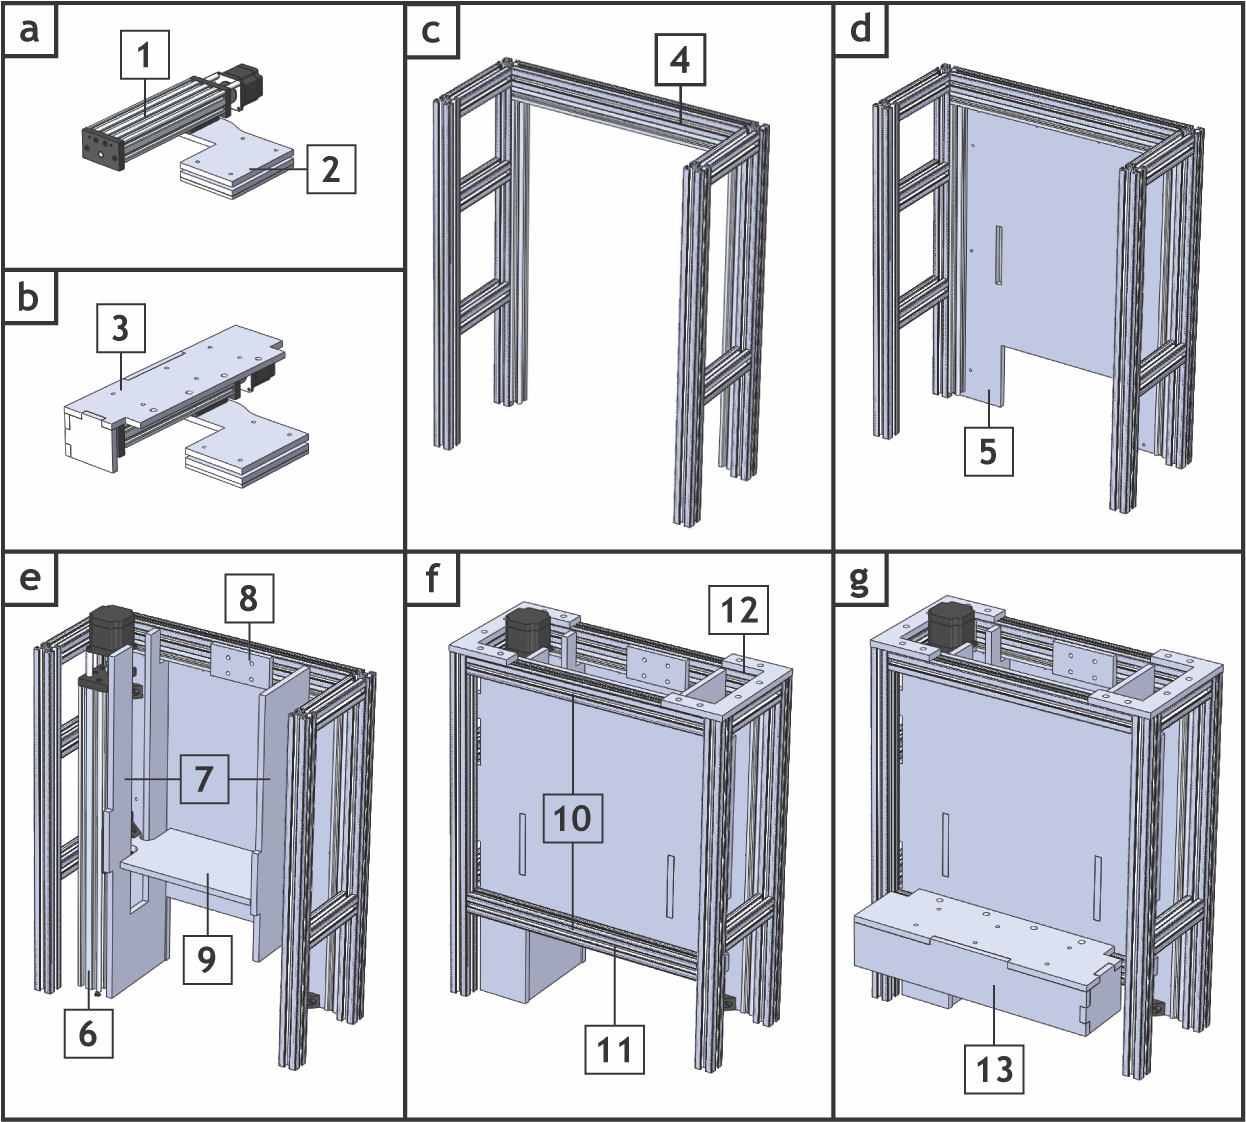
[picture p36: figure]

Figure 2: Assembly process for crosslinker module (a-g). Parts: linear stage (1) with mask (2) and enclosure (3), frame (4), side wall (5), linear stage (6), back wall (7), holder for end stop (8), LED panel (9), frame (10), side wall (11), connector plate (12), and gradient slider assembly (13).

### 4 Storage module

The assembly process for the storage module is depicted in Figure 3.

A storage module has been designed and developed to store well plates or to trash used well plates (e.g. after washing steps). Plates are stored within a rack unit and are positioned onto the transport module by a gripper unit.

Timing | 3 – 5 days
Materials | linear actuators for module as specified in BOM, 20x20mm and 30x30mm aluminium profiles, screws (M3, M5, M6), clamping angles, tee nuts for M5 and M6, NEMA23 stepper motors, cable housing, laser cut parts
Equipment | M3, M5, M6 Allen key
Critical | cutting surface of aluminium profile should be straight
1| | Laser cut acrylic plates as listed in the BOM
2| | Assemble the two linear actuators³
3| | Assembly gripper unit by connecting the 250mm linear belt & pinion actuator with the 20x20mm profile and the gripper plate. The length of the profile can be adjusted according to the depth of the storage module
4| | Assembly rack unit by attaching the four 20x20mm profiles to the laser cut plates which serve as holders for the well plate, and attach side plates (back, left, right)
5| | For the main storage module, connect 30x30mm aluminium profiles and insert holding frame for rack unit
6| | Connect 500mm linear actuator to the back of the module and attach gripper unit
7| | Attach missing profiles on the right side to the base frame

3 https://www.youtube.com/watch?v=tLozVt_CjXQ

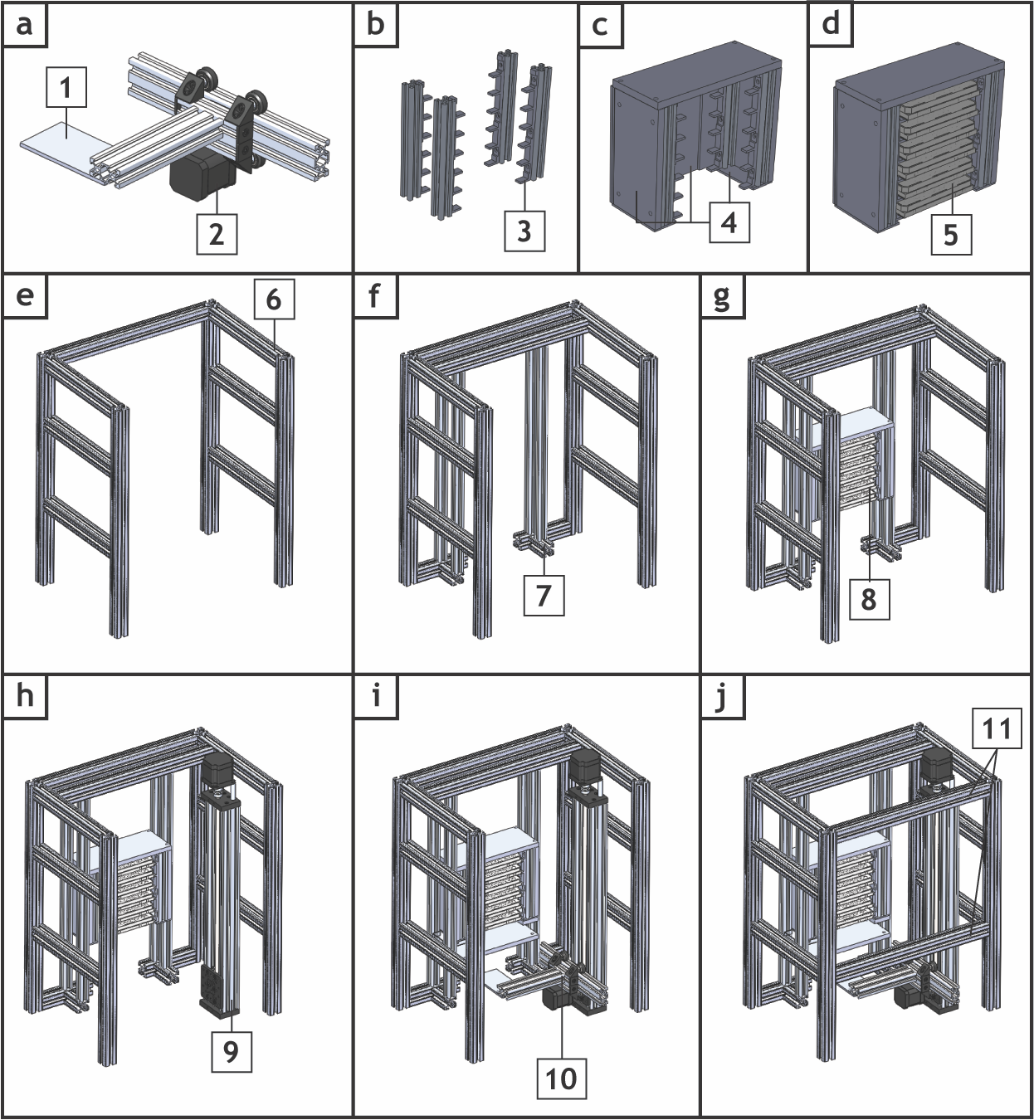
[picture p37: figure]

Figure 3: Assembly process for storage module (a-j). Parts: gripper plate (1), linear stage (2), shelf plates (3) for rack unit (4) to store well plates (5), main frame (6), profile frame for rack unit (7), rack unit (8), linear stage (9) with gripper unit (10), and enclosed frame (11).

### 5 Electrical control box

The main objective of this section is to provide a summary of the electrical work required to connect the stepper motors and end stops as well as to wire the smoothieboard and Arduino (Figure 4). For beginners, introductions to electricity⁴

, soldering⁵ and wiring⁶,7 are recommended before starting with the electrical assembly work. A dedicated control box was designed to comply with the requirements of the university’s Health and Safety guidelines. The main power circuit is a 12V circuit, which is considered as a low-voltage application in most countries. The number of the required components (e.g. control board) are selected based on the number of hardware modules and the required functionalities (e.g. valve).

Timing | 1 week for control box including electrical work
Materials | 2 and 4 core cable, solder, solder wick, heat shrink, ferrules crimper, laser cut plates
Equipment | fine (or flat tip) soldering iron, tweezers, optical microscope to inspect soldered connections, wire cutters, wire strippers, heat gun, multimeter
Caution | use approved or provided ferrules, since ferrule failure can result in wire creeping causing loose wires which may create short circuits
Critical | before starting with connecting the control board(s), familiarize yourself with the wiring diagram (see supplements); check with the Health and Safety department, if electrical work can be executed without a license or if qualified industrial electricians are required to connect the components
1| | If additional electrical components have been added into the control box, modify the control box geometry to accommodate all parts
2| | Laser cut acrylic plates for housing
3| | Drill threaded M3 or M5 holes into the base to attach electrical parts

4 https://learn.sparkfun.com/tutorials/electric-power/all
5 https://learn.adafruit.com/adafruit-guide-excellent-soldering 6 https://learn.sparkfun.com/tutorials/working-with-wire/all 7 https://learn.adafruit.com/wires-and-connections

4| Connect electrical parts to the base using M3 and M5 screws, starting with the power supply, control board, Arduino, valve, and breadboards

5| Start to connect electrical parts to each other according to the electrical circuit:

- Check Vin and GND connections to prevent a short circuit
- Use provided ferrules or connectors to connect wires
6| Connect main power to power supply, switch power on, and check if any LEDs of the smoothieboard are ON. If not, check troubleshooting list for power supply issues⁸
7| | Connect electrical parts of hardware modules to control board
7.1| | Connect the stepper motors to the control board.
- Locate A, A’, B and B’ wires from each of the stepper motors
- Insert wires to the stepper motor top connector according to the provided instructions⁹
- Continue until all stepper motors are connected
7.2| Connect the end stops to the control board
- Locate GND and Signal of each end stop
- Insert wires to the end stop top connector according to the provided instruction¹⁰
- Continue until all end stops are connected
7.3| Connect valve and LEDs to the control board
- Locate GND and Vin of each part
- Insert wires to MOSFET connectors
8| | Connect Arduino to the two temperature probes and two MOSFETs as shown in the electrical circuit schematics
9| | Optional: Install two fans, connected to the main power supply, for air cooling within the control box

8 http://smoothieware.org/troubleshooting#power-supply-problems
9 http://smoothieware.org/stepper-motors
10 http://smoothieware.org/endstops

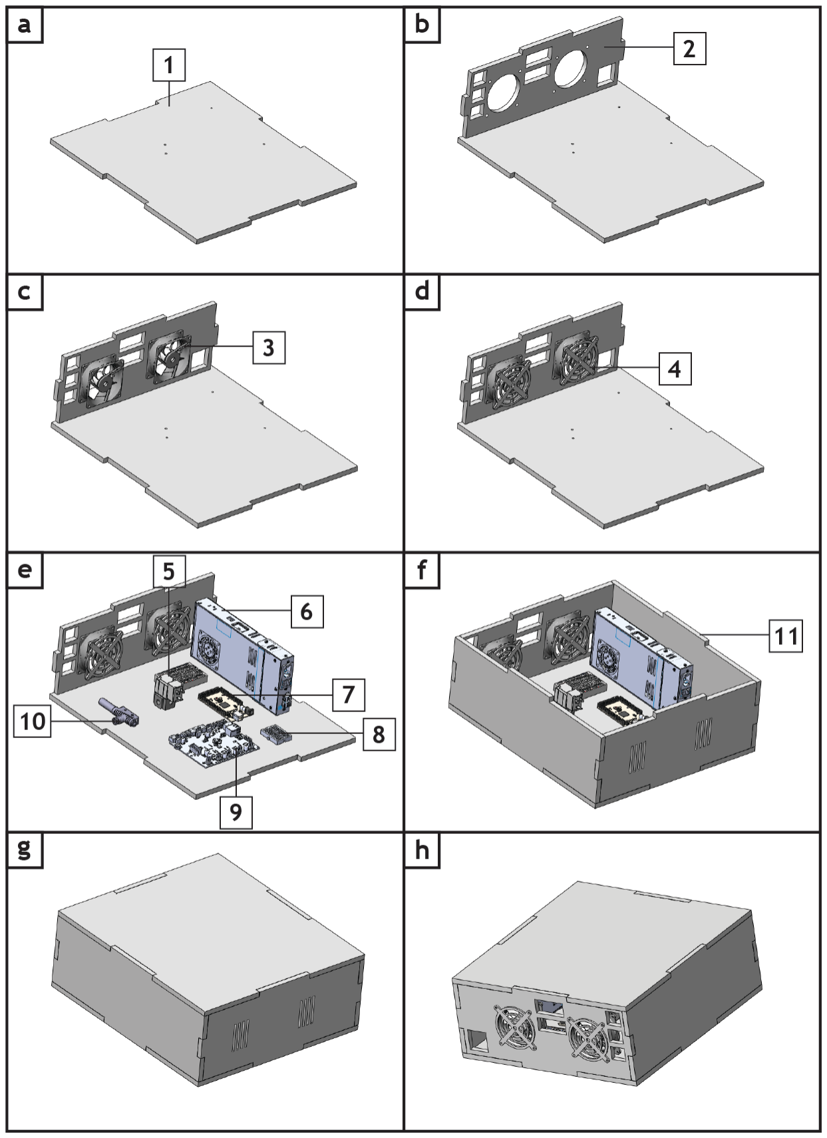
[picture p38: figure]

Figure 4: Assembly process for the control box (a-h): Parts: acrylic base plate (1), acrylic back wall (2) with fans (3) and fan grids (4), valve (5), power supply (6), Arduino MEGA, (7) bread board (8), smoothieboard (9), vacuum ejector (10), acrylic side walls (11).

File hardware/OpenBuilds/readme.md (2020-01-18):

The [SolidWorks part library]  (https://openbuilds.com/projectresources/solidworks-2014-parts-library.160/) was uploaded with OpenBuilds permission.

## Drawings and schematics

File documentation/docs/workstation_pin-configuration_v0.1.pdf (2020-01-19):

# Legend

# signal

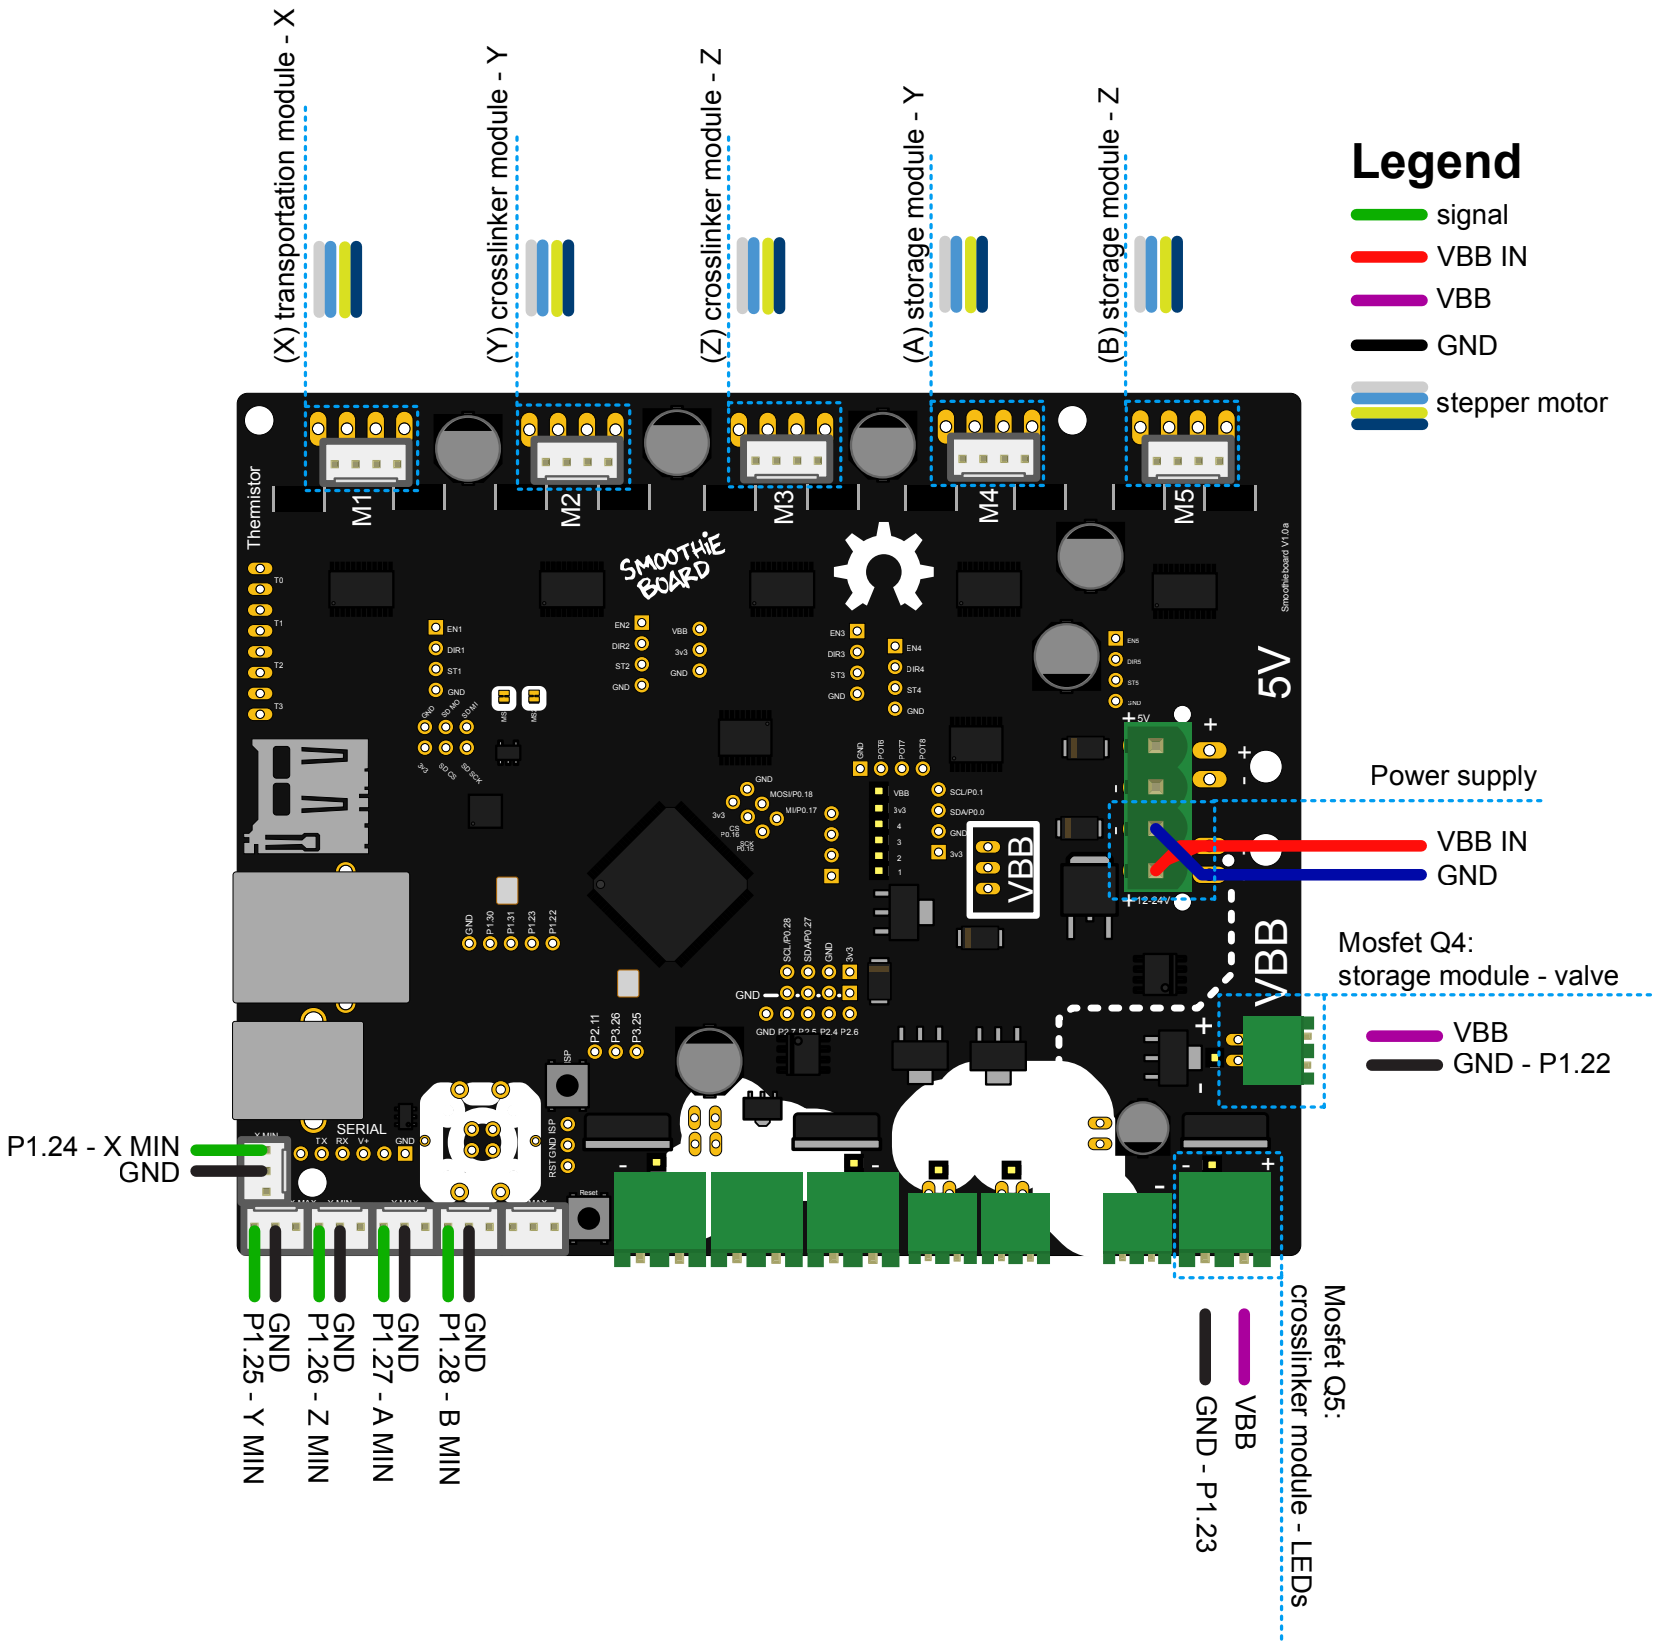
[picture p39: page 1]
Reset; X MAX Y MIN; Y MAX; Z MIN; Z MAX; X MIN; SERIAL; ISP; GND P2.7 P2.5 P2.4 P2.6; GND; SCL/P0.28; SDA/P0.27; SD SCK; DIR1; DIR2; VBB; DIR3; DIR4; DIR5; Smoothieboard V1.0a; Thermistor; GND MOSI/P0.18 MI/P0.17; SCK P0.15; POT6; POT7; POT8; SDA/P0.0; SCL/P0.1; GND M¹; stepper motor; VBB GND; P1.24 - X MIN; VBB GND - P1.22; P1.25 - Y MIN; P1.26 - Z MIN; P1.27 - A MIN; P1.28 - B MIN; GND - P1.23; Mosfet Q5:; (X) transportation module - X; (Y) crosslinker module - Y; (Z) crosslinker module - Z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

Power supply
VBB IN
GND
Mosfet Q4:
storage module - valve

ISP GND RST

crosslinker module - LEDs

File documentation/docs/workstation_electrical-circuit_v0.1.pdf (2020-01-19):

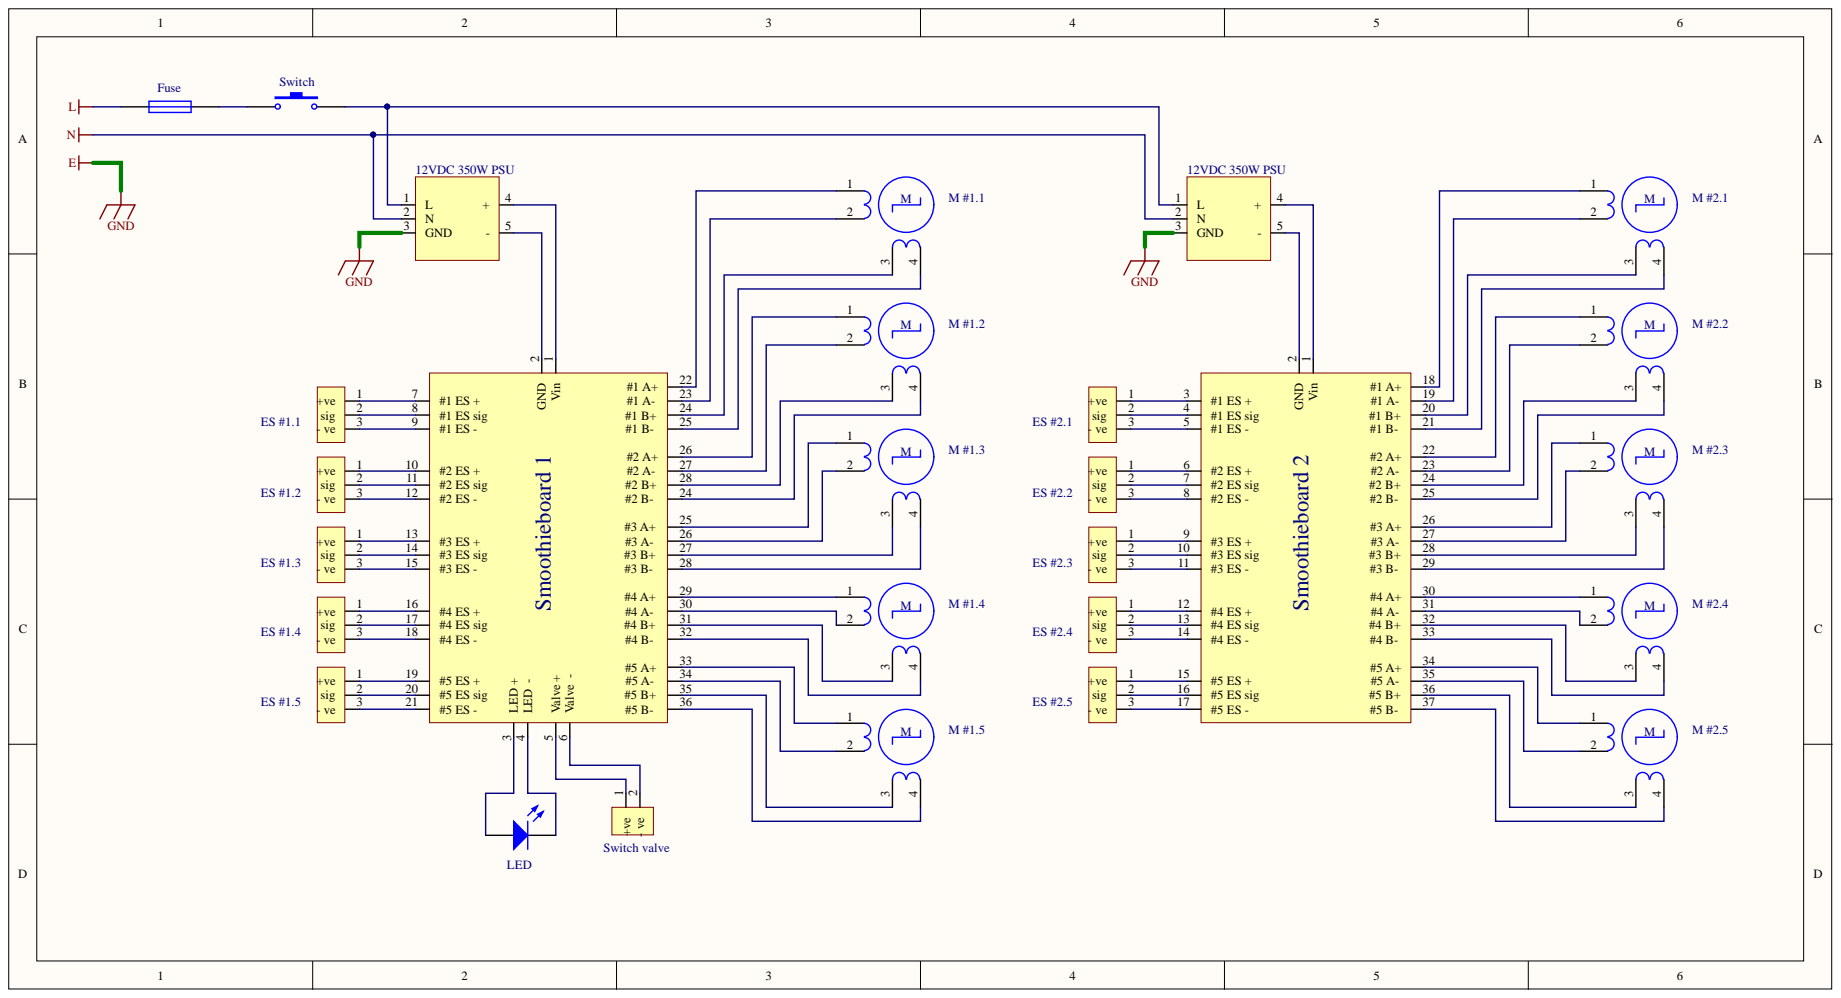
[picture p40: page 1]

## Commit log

2020-01-19 CAD models
    [1002_Motor_Mount_Plate.SLDPRT, 8mm Acme Nut Block.SLDPRT, 8mm leadscrew 290mm.SLDPRT, 8mm leadscrew 540mm.SLDPRT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]
2020-01-20 add moduleFrame
    [Profile_30x30mm_100mm.SLDPRT, Profile_30x30mm_1130mm.SLDPRT, Profile_30x30mm_140mm.SLDPRT, Profile_30x30mm_250mm.SLDPRT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]
2020-01-20 zenodo upload and doi batch
    [workstation_bom__v0.1.xlsx]
